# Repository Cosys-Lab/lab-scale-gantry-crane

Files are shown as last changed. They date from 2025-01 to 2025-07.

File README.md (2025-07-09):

# Lab-scale Gantry Crane Digital Twin Exemplar

This repository describes a lab-scale gantry crane digital twin exemplar. This exemplar was used in a couple of our [publications](#publications). This readme only contains basic information, for the complete documentation, head to [github pages](https://Cosys-Lab.github.io/lab-scale-gantry-crane/).

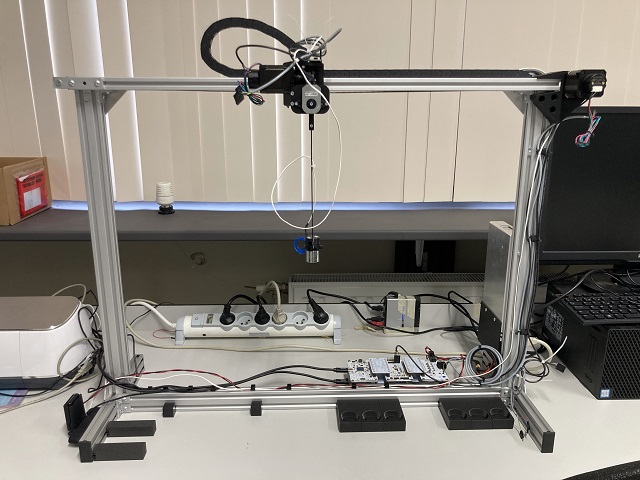
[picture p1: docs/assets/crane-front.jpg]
The gantry crane


The repository is structured as follows:

- [BOM](BOM/): the Bill-of-Materials of the crane.
- [C4-diagrams](C4-diagrams/): C4 diagrams of the crane's software used in the EDTConf submitted exemplar paper.
- [CAD](CAD/): CAD models of the crane in Fusion360, as well as 3MF exports for 3D printing.
- [arcadia](arcadia/): Capella models of the crane used in the SpaceRaise doctoral school.
- [arduino](arduino/): KiCad project of an optional Arduino shield that simplifies connecting the sensors of the crane, and accompanying code.
- [docker](docker/): A Docker compose file and associated files allowing for easy setup of the necessary background services.
- [docs](docs/): docs for creating the GitHub pages with MkDocs
- [examples](examples/): Examples of the Python module that controls the crane.
- [gantrylib](gantrylib/): The Python module controlling and monitoring the crane.
- [tests](tests/): Tests of the gantrylib module.

## Hardware Quickstart

Refer to the [build guide](https://cosys-lab.github.io/lab-scale-gantry-crane/build/) on GitHub Pages.

## Software Setup

### Python

Install Python. On Windows, preferably use Python 3.13 or higher, since earlier versions have a low resolution (only 15.6 ms) of the `time()` and `datetime.now()` functions, which are used often in the code.

Install the `gantrylib` module locally as editable installation. From the root of the repository folder, run:

    python -m pip install -e .

### Background services

The software relies on a TimescaleDB database, a Grafana dashboard and, optinally an MQTT broker. The setup files of all of these are contained in the [docker](docker/) folder. Assuming docker and docker compose are installed, from the docker folder, it suffices to run:

    docker compose up

The containers can then be started and stopped with:

    docker compose stop
    docker compose start

To remove the containers and the network connecting them, run:

    docker compose down

The config is exceptionally insecure, since all of the default usernames/passwords are used. If this is a problem, do change them.

#### TimeScaleDB
- address: localhost
- port: 5432
- user: postgres
- password: postgres
- database: gantrycrane

#### Grafana Dashboard
- address: localhost
- port: 3000
- user: admin
- password: admin (On first login via http://localhost:3000, you will be prompted to change the password. Nothing blocks you from reusing the old password though.)

#### MQTT
- address: localhost
- port: 1883
- user: not necessary, anonymous connections are allowed

The MQTT broker is really only needed if you want to run the TrajectoryGenerator service in its MQTT mode. Ofter services (Simulator, Validator) have in this release not yet been implemented in MQTT mode.

## Software quickstart

Assuming you went through the [software setup](#software-setup) and built the crane according to the [hardware quickstart](#hardware-quickstart), the fastest way to get the crane to do something is using the [run_with_hmi.py](examples/run_with_hmi.py) example. A short video demonstrating the example can be found on [youtube](https://youtu.be/BBAWoA0mC9U).

You will have to configure [crane-properties.yaml](examples/crane-properties.yaml) for your specific installation, more specifically, specify the serial ports of the two motor controller boards. Unfortunately, the Trinamic devkits don't offer a unique ID that allows you to identify them, therefore we recommend plugging in the boards one by one, and noting down the serial ports that appear as you plug them in (in `device manager/Ports (COM & LPT)` in Windows, or under `/dev/tty*` in Linux.)

Once you have noted down those ports, update the following two fields in the config:

    cart_motor_port: COM13
    ...
    hoist_motor_port: COM8

You can now run the example.

Upon first starting, it will home the cart and hoist motor. Homing the cart motor happens automatically, homing the hoist motor must be done with some manual user input. The script prompts you to confirm this on the command line. Afterwards you will see the simple HMI interface that allows you to move the crane.

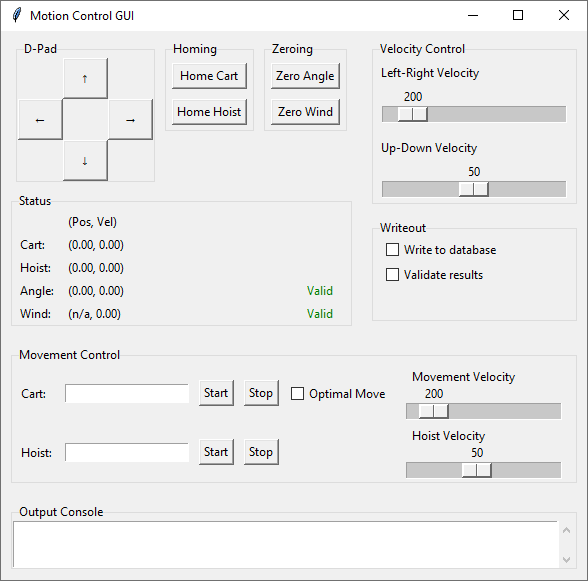
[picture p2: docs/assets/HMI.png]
HMI Screenshot


## Publications

Below are publications in which this exemplar was used:

1. J. Mertens and J. Denil, *Localizing Faults in Digital Twin Models by Using Time Series Classification Techniques*, 2024 Winter Simulation Conference (WSC), IEEE, Dec. 2024, pp. 2868–2879. [https://doi.org/10.1109/wsc63780.2024.10838825](https://doi.org/10.1109/wsc63780.2024.10838825)

2. J. Mertens, S. Klikovits, F. Bordeleau, J. Denil, and Ø. Haugen, *Continuous Evolution of Digital Twins using the DarTwin Notation*, Software and Systems Modeling, p. 22, Nov. 2024. [https://doi.org/10.1007/s10270-024-01216-7](https://doi.org/10.1007/s10270-024-01216-7)

3. J. Mertens and J. Denil, *Reusing model validation methods for the continuous validation of digital twins of cyber-physical systems*, Software and Systems Modeling, p. 23, Oct. 2024. [https://doi.org/10.1007/s10270-024-01225-6](https://doi.org/10.1007/s10270-024-01225-6)

4. J. Mertens and J. Denil, *Digital-twin Co-evolution using Continuous Validation*, In Proceedings of the ACM/IEEE 14th International Conference on Cyber-Physical Systems (with CPS-IoT Week 2023), ICCPS ’23, San Antonio, TX, USA: ACM, 2023, pp. 266–267. [https://doi.org/10.1145/3576841.3589628](https://doi.org/10.1145/3576841.3589628)

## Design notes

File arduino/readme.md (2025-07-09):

# Arduino

We use an Arduino Uno for monitoring and controlling the angle measuring encoder, the anemometer, the electromagnet (and the fischertechnik conveyor belt).

The folders contain:

- [arduino-shield-hardware](arduino-shield-hardware/)  
  The KiCad files of the optional Arduino shield.
- [arduino-shield-software](arduino-shield-software/)  
  The software to flash on the Arduino.
- [mqtt-wrapper](mqtt-wrapper/)  
  An MQTT wrapper around the Serial interface of the Arduino. Not needed when you only want to monitor the sensors.

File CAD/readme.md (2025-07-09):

# CAD

Contains the autodesk Fusion360 models of the crane. The [3MFs](3MFs/) folder contains exports of the 3D-printable files.

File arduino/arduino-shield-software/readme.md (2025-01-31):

Arduino code for an Arduino with the Conveyor shield V1.0 connected to 
the Fischertechnik conveyorbelt.

The command structure is described below

# G1 - Move indefinitely
## Description

The `G1` command moves the conveyor forwards or backwards indefinitely.

## Usage

`G1 [dir]`

### Parameters

[dir]: `F` for forwards, `B` for backwards.

## Example

`G1 F` # move forward indefinitely

# G2 - Move amount of pulses

## Description

The `G2` command moves the conveyor forwards or backwards a certain amount of pulses/steps.
one pulse is 1/8th of a rotatino of the conveyor's axle.

## Usage

`G1 [dir][pulses]`

### Parameters

[dir]: `F` for forwards, `B` for backwards.
[pulses]: number of pulses to move

## Example

`G1 F4` # move forward 4 pulses

# G3 - Move untill sensor

## Description

The `G3` command moves the conveyor forwards or backwards until the object
on the conveyor meets the start/end sensor.

## Usage

`G3 [dir]`

### Parameters

[dir]: `F` for forwards, `B` for backwards.

## Example

`G3 F` # move forward until the end sensor is triggered.

# G4 - Query Sensor State

## Description

The `G4` command queries the sensor (start, stop and pulse counter) state.

## Usage

`G4`

### Returns

`START_SENSOR: [1/0], END_SENSOR [1/0], PULSE_COUNT: [integer]`

## Example

`G4` # request sensor state
`START_SENSOR: 1, END_SENSOR 0, PULSE_COUNT: 40` # printer returns

# G5 - Stop movement

## Description

The `G5` command stops the conveyor.

## Usage

`G5`

# G6 - Electromagnet Control

## Description

The `G6` command controls the electromagnet

## Usage

`G6 [on/off]`

### Parameters

[on/off]: 0 to turn off, any other value to turn on.

## Example

`G6 1` # turn magnet on
`G6 0` # turn magnet off

# Other notes:

When a command is received that does not output data to the printer, 
it will return `OK [repeat command]` on the terminal

When an unknown command is received, it will return `NOK [repeat command]`

# Continuous angle output

The arduino also continuously measures the angle and the angular velocity
of the encoder and outputs it at a rate of 100 Hz.

This output has the shape `A: SX.XX,V: SY.YY`, where S is the optional
minus (-) sign, and the angle and angular velocity are printed with 2
decmial places. 

e.g. `A: -360.00,V: 10.15`

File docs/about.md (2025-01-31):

# about.md

Pages maintained by Joost Mertens
In case of question, feel free to get in touch by email or use the github issues: joost.mertens@uantwerpen.be

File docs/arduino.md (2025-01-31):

# arduino.md

## Prerequisites

Install following dependencies in the arduino IDE:

[Encoder](https://github.com/PaulStoffregen/Encoder)
[PinChangeInterrupt](https://github.com/NicoHood/PinChangeInterrupt/#pinchangeinterrupt-table)

## Explanation

In a nutshell: there are two arduino scripts

* one to measure angles with the encoder
* one to control the electromagnet (with additional functions)
    * this script requires you to build the arduino shield, for which KiCad files are provided.

In the future all of this code should be placed on one Arduino,
and the shield updated to a V2, which is future work.

## MQTT Wrapper

The shield was actually used to control a Fischertechnik conveyor belt with the arduino,
(to be detailled more) The command interface over serial can be found in the readme.md file in the folder.
We also provide an MQTT wrapper around it such that you can interface with Python or any other general purpose programming language.
TODO: document.

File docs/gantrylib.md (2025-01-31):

# gantrylib.md

## crane

### Crane

::: gantrylib.crane.Crane

## motors

### Motor

::: gantrylib.motors.Motor

### Stepper

::: gantrylib.motors.Stepper

### GantryStepper

::: gantrylib.motors.GantryStepper

### HoistStepper

::: gantrylib.motors.HoistStepper

## trajectory_generator

### TrajectoryGenerator

::: gantrylib.trajectory_generator.TrajectoryGenerator

## gantry_controller

## GantryController

::: gantrylib.gantry_controller.GantryController

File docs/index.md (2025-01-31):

# Lab Scale Gantry Crane Docs

crane-front

This is the documentation of the lab scale gantry crane. It is a little gantry crane that has been used in various papers as a demonstrator. The documentation covers the build of the crane, the accompanying `gantrylib` module and exmaples using this module.

## Documentation layout

* Home: this page
* Build: building instructions for the physical part of the crane.
* Arduino: documentation of the arduino scripts
* Examples: documentation of the examples
* gantrylib: api reference for the `gantrylib`

## Software prerequisites

### Installing gantrylib

The examples rely on the `gantrylib` module. Since there's no official release (yet) we recommend installing it in editable mode, this also allows for on the fly code changes. In the root of this repository run:

    python -m pip install -e .

We recommend doing so in a virtual environment.

### Arduino sketches

To open and flash the Arduino sketches you can install the [Arduino IDE](https://www.arduino.cc/)

### Opening CAD files

All CAD files are made with [Fusion360](https://www.autodesk.com/products/fusion-360/free-trial)
It's free for personal use. Your educational institution likely also has a license.

All files have already been exported to 3MF files, so you only need Fusion360 when you want to make edits.

### Viewing the docs offline

The docs are built with `MkDocs`. If you want to host those locally rather than view them on GitHub pages you should additionally install it.

    python -m pip install mkdocs mkdocstrings[python]

You can view the docs by running 

    mkdocs serve

Then opening http://127.0.0.1:8000/

## Hardware prerequisites

### 3D Printer

Some parts of the crane need to be 3D printed. To do so you need a 3D printer and accompanying slicer.

For reference: our parts where printed on Prusa i3 MK4's and sliced with [PrusaSlicer](https://www.prusa3d.com/page/prusaslicer_424/)

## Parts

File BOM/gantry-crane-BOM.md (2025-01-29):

# crane-BOM.md

## Bill of Materials (BOM)

This Bill of Materials (BOM) lists all the components required for this hardware project, including part numbers, descriptions, and suppliers.
This BOM in markdown format is generated from the original in Excel format. [BOM/crane_BOM.xlsx](../BOM/crane_BOM.xlsx)

### Sheet Hardware

| description                                            | supplier | supplier part number | quantity | price (€)         | total (€) | link                                                                                                                                                  |
|--------------------------------------------------------|----------|----------------------|----------|-------------------|-----------|-------------------------------------------------------------------------------------------------------------------------------------------------------|
| V-slot carriage                                        | ALUX     | V-slot gantry        | 1        | 5.95              | 5.95      | https://www.aluxprofiel.nl/v-slot-plaat/a4022                                                                                                         |
| 2040 cover plate                                       | ALUX     | 2040-cover           | 6        | 0.29              | 1.74      | https://www.aluxprofiel.nl/afdekkap-2040/a3586                                                                                                        |
| Aluminium profile 2040 V-slot 300mm                    | ALUX     | 2040                 | 2        | 1.99              | 3.98      | https://www.aluxprofiel.nl/aluminium-constructieprofiel-2040-v-slot/a3664                                                                             |
| Aluminium profile 2040 V-slot 560mm                    | ALUX     | 2040                 | 2        | 3.71              | 7.42      | https://www.aluxprofiel.nl/aluminium-constructieprofiel-2040-v-slot/a3664                                                                             |
| Aluminium profile 2040 V-slot 800mm                    | ALUX     | 2040                 | 1        | 5.3               | 5.3       | https://www.aluxprofiel.nl/aluminium-constructieprofiel-2040-v-slot/a3664                                                                             |
| Aluminium profile 2040 V-slot 760mm                    | ALUX     | 2040                 | 1        | 5.97              | 5.97      | https://www.aluxprofiel.nl/aluminium-constructieprofiel-2040-v-slot/a3664                                                                             |
| Connection plate Flat 20x80 - 4 holes                  | ALUX     | plate2080            | 1        | 0.69              | 0.69      | https://www.aluxprofiel.nl/verbindingsplaat-20x80/a3804                                                                                               |
| Connection plate T-shaped 60x60 - 5 holes              | ALUX     | T-plate6060          | 2        | 0.99              | 1.98      | https://www.aluxprofiel.nl/verbindingsplaat-t-60x60-5-gaten/a3810                                                                                     |
| Connection plate L-shaped 60x60 - 5 holes              | ALUX     | L-Plate6060          | 2        | 0.99              | 1.98      | https://www.aluxprofiel.nl/verbindingsplaat-l-60x60-5-gaten/a3809                                                                                     |
| Button head hex bolt M5x8                              | ALUX     | ISO 7380-M5x8        | 80       | 0.07              | 5.6       | https://www.aluxprofiel.nl/laagbolkopschroef-m5x8/a3794                                                                                               |
| T-slot nut M5                                          | ALUX     | 6-4-M5               | 80       | 0.2               | 16        | https://www.aluxprofiel.nl/inklikmoer-t-sleuf-6-m5/a3665                                                                                              |
| Rubber feet                                            | ALUX     | 9004                 | 6        | 0.79              | 4.74      | https://www.aluxprofiel.nl/rubber-voet/a3746                                                                                                          |
| Aluminium corner bracket 2020                          | ALUX     | 2020L-Alu            | 12       | 0.99              | 11.88     | https://www.aluxprofiel.nl/aluminium-verbindingshoek-2020/a3729                                                                                       |
| 2GT W6 Belt 2000mm                                     | 3DJake   | 2GT W6 2000 mm       | 1        | 5.83              | 5.83      | https://www.3djake.com/creality-3d-printers-spare-parts/belt-kit                                                                                      |
| 20 teeth 2GT Belt Pulley for 5mm shaft                 | 3DJake   | 2GT-20 5mm           | 1        | 2.49              | 2.49      | https://www.3djake.com/artillery/belt-pulley                                                                                                          |
| 625 2RS Bearing                                        | Conrad   | 198831 - 62          | 2        | 3.96              | 7.92      | https://www.conrad.be/nl/p/ubc-bearing-625-2rs-groefkogellager-radiaal-boordiameter-5-mm-buitendiameter-16-mm-toerental-max-24000-omw-min-198831.html |
| igus E-Kette® E2 micro Serie 06 06.10.018.0 Drag chain | Conrad   | 740611 - 62          | 1        | 28.09             | 28.09     | https://www.conrad.be/nl/p/igus-e-kette-e2-micro-serie-06-06-10-018-0-kabelrups-voor-kleine-buigradius-740611.html                                    |
| M2.5x8 countersunk bolt                                |          |                      | 1        |                   |           |                                                                                                                                                       |
| M2.5x12 bolt (can be countersunk or not)               |          |                      | 2        |                   |           |                                                                                                                                                       |
| M2.5x20 countersunk bolt                               |          |                      | 1        |                   |           |                                                                                                                                                       |
| M2.5 nut                                               |          |                      | 4        |                   |           |                                                                                                                                                       |
| M3x10 bolt (not countersunk)                           |          |                      | 10       |                   |           |                                                                                                                                                       |
| M3x20 countersunk bolt                                 |          |                      | 3        |                   |           |                                                                                                                                                       |
| M3 nut                                                 |          |                      | 2        |                   |           |                                                                                                                                                       |
| M4x12 countersunk bolt                                 |          |                      | 2        |                   |           |                                                                                                                                                       |
| M4x20 countersunk bolt                                 |          |                      | 2        |                   |           |                                                                                                                                                       |
| M4 nut                                                 |          |                      | 4        |                   |           |                                                                                                                                                       |
| M5x10 countersunk bolt                                 |          |                      | 2        |                   |           |                                                                                                                                                       |
| M5x16 countersunk bolt                                 |          |                      | 3        |                   |           |                                                                                                                                                       |
| M5x20 countersunk bolt                                 |          |                      | 2        |                   |           |                                                                                                                                                       |
| M5 nut                                                 |          |                      | 7        |                   |           |                                                                                                                                                       |
| Nuts and bolts: check fusion360 for dimensions         |          |                      |          |                   |           |                                                                                                                                                       |
|                                                        |          |                      |          | total (excl. VAT) | 117.56    |                                                                                                                                                       |

### Sheet - Electronics

| description                                                                       | supplier | supplier part number     | quantity | price (€)         | total (€) | link                                                                                                                           |
|-----------------------------------------------------------------------------------|----------|--------------------------|----------|-------------------|-----------|--------------------------------------------------------------------------------------------------------------------------------|
| Trinamic TMC4671-2A24V-EV-KIT (motor controller development kit)                  | Mouser   | 700-MC46712A24VEVKIT     | 2        | 297.53            | 595.06    | https://eu.mouser.com/ProductDetail/ADI-Trinamic/TMC4671-2A24V-EV-KIT?qs=TuK3vfAjtkVo6zoElLhaVQ%3D%3D                          |
| Trinamic QSH4218-51-10-049-10k stepper motor                                      | Mouser   | 700-QSH4218511004910     | 2        | 149.03            | 298.06    | https://eu.mouser.com/ProductDetail/ADI-Trinamic/QSH4218-51-10-049-10k?qs=QNEnbhJQKvbElhB2hkRfrg%3D%3D                         |
| Arduino Uno                                                                       | Mouser   | 782-A000066              | 2        | 26.22             | 52.44     | https://eu.mouser.com/ProductDetail/Arduino/A000066?qs=BC3YYPaifMrIue9b%252BHtKQg%3D%3D                                        |
| Molex 502380-0900 connector (for motors)                                          | Mouser   | 538-502380-0900          | 2        | 0.298             | 0.596     | https://eu.mouser.com/ProductDetail/Molex/502380-0900?qs=FtUJHUU4yUnSF7MTpEglZg%3D%3D                                          |
| Molex 502381-0000 pin (for motors)                                                | Mouser   | 538-502381-0000-CT       | 100      | 0.044             | 4.4       | https://eu.mouser.com/ProductDetail/Molex/502381-0000-Cut-Strip?qs=SMSg0crzni%2Fg42ifI25maw%3D%3D                              |
| Molex 16-02-0086  SL Crimp terminla female (for motor, motor drivers and encoder) | Mouser   | 538-70021-1021           | 100      | 0.079             | 7.9       | https://eu.mouser.com/ProductDetail/Molex/16-02-0086-Cut-Strip?qs=Ky1INM14uHolwHYRokZMPQ%3D%3D                                 |
| Molex 70021-1021 SL Crimp terminal male (for motors)                              | Mouser   | 538-16-02-0086-CT        | 100      | 0.079             | 7.9       | https://eu.mouser.com/ProductDetail/Molex/70021-1021?qs=PEbA6nSK%252BIWnZ1R%252Bv0zaCA%3D%3D                                   |
| Molex 50579405 SL Crimp housing (for AMT102 encoder)                              | Mouser   | 538-50-57-9405           | 1        | 0.314             | 0.314     | https://eu.mouser.com/ProductDetail/Molex/50-57-9405?qs=u6Gr9%2FNt%252B%2F%252BwqrO8nkfpaQ%3D%3D                               |
| Molex 50579005 SL Crimp housing (for motors and motor drivers)                    | Mouser   | 538-50-57-9005           | 6        | 0.447             | 2.682     | https://eu.mouser.com/ProductDetail/Molex/50-57-9005?qs=hSmm4fxMIuNcn%252B35N0E0lA%3D%3D                                       |
| Molex 50579002 SL Crimp housing (for electromagnet)                               | Mouser   | 538-50-57-9002           | 1        | 0.276             | 0.276     | https://eu.mouser.com/ProductDetail/Molex/50-57-9002?qs=hSmm4fxMIuPN0%252B32zyqW%252Bw%3D%3D                                   |
| Same Sky AMT102-V encoder                                                         | Mouser   | 490-AMT102-V             | 1        | 21.69             | 21.69     | https://eu.mouser.com/ProductDetail/Same-Sky/AMT102-V?qs=WyjlAZoYn533PQfgnorrMg%3D%3D                                          |
| Qualtek 764-00/002 AC Power Entry Module                                          | Mouser   | 562-764-00/002           | 1        | 7.52              | 7.52      | https://eu.mouser.com/ProductDetail/Qualtek/764-00-002?qs=uN5Dye%252BOwiXfVfVI0dfkHA%3D%3D                                     |
| Qualtek 364002-D01-HB1 AC Power cable                                             | Mouser   | 562-364002-HB1           | 1        | 8.36              | 8.36      | https://eu.mouser.com/ProductDetail/Qualtek/364002-D01-HB1?qs=tENXCkUKGaHfbZG0hkGDSQ%3D%3D                                     |
| Adafruit 5V Electromagnet                                                         | Mouser   | 485-3873                 | 1        | 9.25              | 9.25      | https://eu.mouser.com/ProductDetail/Adafruit/3873?qs=qSfuJ%252Bfl%2Fd4HCVDk1VD%2FzQ%3D%3D                                      |
| SparkFun Accessories XT60 Connectors Male/Female Pair                             | Mouser   | 474-PRT-10474            | 1        | 1.4               | 1.4       | https://eu.mouser.com/ProductDetail/SparkFun/PRT-10474?qs=WyAARYrbSnYJaRDMiD9g2w%3D%3D                                         |
| 24V Power Supply for Creality Ender 3 s1                                          | 3DJake   | Power Supply, Ender 3 s1 | 1        | 40.32             | 40.32     | https://www.3djake.com/creality-3d-printers-spare-parts/power-supply-1?sai=14488                                               |
| Kabeltronik Sensorcable Sensocord® 5 x 0.09 mm² (quantity in meters)              | Conrad   | 323819 - 62              | 5        | 5.78              | 28.9      | https://www.conrad.be/nl/p/kabeltronik-24205d800-1-sensorkabel-sensocord-5-x-0-09-mm-zwart-per-meter-323819.html               |
| Kabeltronik PURtronic Highflex cable 4 x 0.14 mm² (quantity in meters)            | Conrad   | 486529 - 62              | 3        | 4.95              | 14.85     | https://www.conrad.be/nl/p/kabeltronik-purtronic-highflex-stuurstroomkabel-4-x-0-14-mm-grijs-213041400-1-per-meter-486529.html |
| Lenovo USB-C to 4 Port USB-A Hub USB-C                                            | Conrad   | 2886621 - 62             | 1        | 14.87             | 14.87     | https://www.conrad.be/nl/p/lenovo-usb-c-to-4-port-usb-a-hub-usb-c-usb-3-2-gen-1-multiport-hub-4-poorten-zwart-2886621.html     |
| Wiring from power supply to motor controllers. 2x16 AWG suffices                  |          |                          |          |                   |           |                                                                                                                                |
| Wiring to electromagnet, thinner cable with 2x24 AWG suffices                     |          |                          |          |                   |           |                                                                                                                                |
|                                                                                   |          |                          |          | total (excl. VAT) | 1116.788  |                                                                                                                                |

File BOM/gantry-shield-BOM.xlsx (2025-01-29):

article | description | qty | price | subtotal | link
637-1N4007 | 1N4007 | 1 | 0.093 | 0.093 | https://www.mouser.be/ProductDetail/Diotec-Semiconductor/1N4007?qs=OlC7AqGiEDmK9mU1uTiCkg%3D%3D
651-1757242 | MSTBA 2,5/ 2-G-5,08 - PCB header | 1 | 0.54 | 0.54 | https://eu.mouser.com/ProductDetail/Phoenix-Contact/1757242?qs=uD%2FdkN7XIa3Ejiz9qDxlzw%3D%3D
651-1757019 | MSTB 2,5/ 2-ST-5,08 - PCB connector | 1 | 2.02 | 2.02 | https://eu.mouser.com/ProductDetail/Phoenix-Contact/1757019?qs=cq3Rj917t3lqr5dPgsHAsg%3D%3D
710-61202621621 | 61202621621 | 1 | 1.03 | 1.03 | https://eu.mouser.com/ProductDetail/Wurth-Elektronik/61202621621?qs=ZtY9WdtwX57AwIRbd5IHkA%3D%3D
710-61202623021 | 61202623021 | 2 | 1.47 | 2.94 | https://eu.mouser.com/ProductDetail/Wurth-Elektronik/61202623021?qs=ZtY9WdtwX57g2sRCs8B%2Fgw%3D%3D
517-3365/26FT | 3365/26-CUT-LENGTH | 1 | 1.15 | 1.15 | https://eu.mouser.com/ProductDetail/3M-Electronic-Solutions-Division/3365-26-CUT-LENGTH?qs=QV10cN0MjFu22vZzOnogAw%3D%3D
522-BS170FTA | BS170F | 1 | 0.632 | 0.632 | https://eu.mouser.com/ProductDetail/Diodes-Incorporated/BS170FTA?qs=%2FU6xRUa2FMDXziIHYnqHVQ%3D%3D
595-TL084HIDR | TL084 SOIC14 | 1 | 0.28 | 0.28 | https://eu.mouser.com/ProductDetail/Texas-Instruments/TL084HIDR?qs=81r%252BiQLm7BTThBPvzBazbA%3D%3D
603-MFR-25FTF52-220R | 220 ohms | 1 | 0.093 | 0.093 | https://eu.mouser.com/ProductDetail/YAGEO/MFR-25FTF52-220R?qs=gt1LBUVyoHnXPrJ70Ki%252BVg%3D%3D
603-MFR-25FTF52-100K | 100k | 5 | 0.093 | 0.465 | https://eu.mouser.com/ProductDetail/YAGEO/MFR-25FTF52-100K?qs=OXzh9Ga2KBF%252BJCQIIZKMHQ%3D%3D
603-MFR-25FTF52-22K | 22k | 4 | 0.093 | 0.372 | https://eu.mouser.com/ProductDetail/YAGEO/MFR-25FTF52-22K?qs=gt1LBUVyoHkUynDsTgGFYw%3D%3D
603-MFR-25FTF52-10K | 10k | 1 | 0.093 | 0.093 | https://eu.mouser.com/ProductDetail/YAGEO/MFR-25FTF52-10K?qs=NNLo%2FHOmKML%2FcyMBYbmnXA%3D%3D
474-PRT-10007 | PRT-10007 | 1 | 1.51 | 1.51 | https://eu.mouser.com/ProductDetail/SparkFun/PRT-10007?qs=WyAARYrbSnYGf8RckgedYg%3D%3D
530-SC-2ABE003F | USB B cable | 1 | 2.26 | 2.26 | https://eu.mouser.com/ProductDetail/Stewart-Connector-Bel/SC-2ABE003F?qs=r5DSvlrkXmIbaXte8fNdQA%3D%3D
 |  |  | total | 13.478

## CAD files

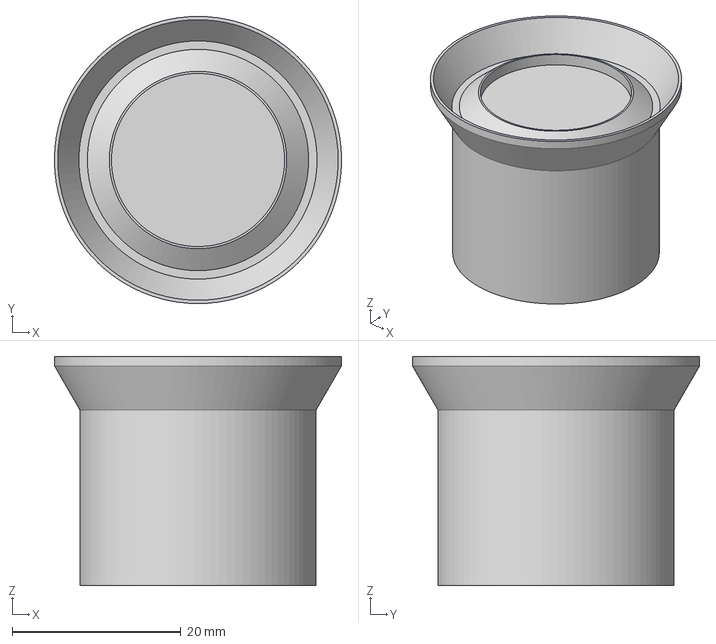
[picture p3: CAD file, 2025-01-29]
CAD/3MFs/stackable-container.3mf
34.0 x 34.0 x 27.1 mm

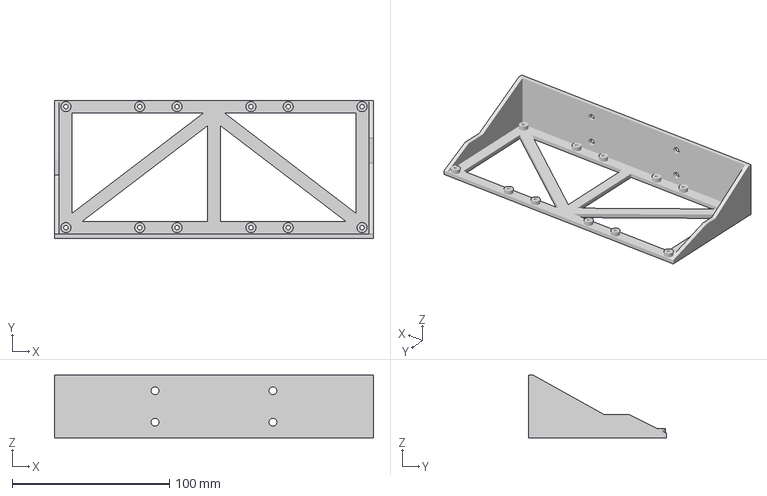
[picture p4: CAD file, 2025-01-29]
CAD/3MFs/motor-driver-mount.3mf
203.0 x 88.0 x 40.0 mm

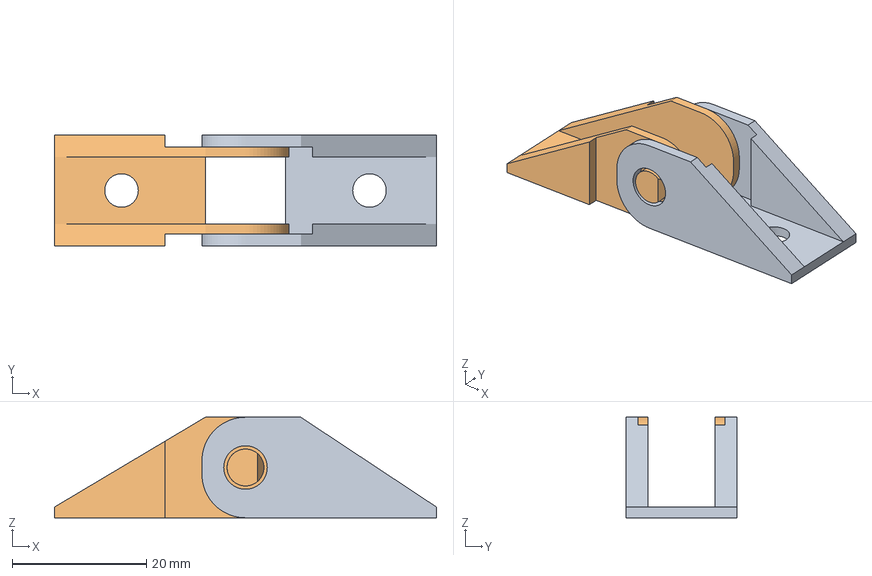
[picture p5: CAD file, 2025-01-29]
CAD/3MFs/chain-link-ends.3mf
57.0 x 16.5 x 15.0 mm

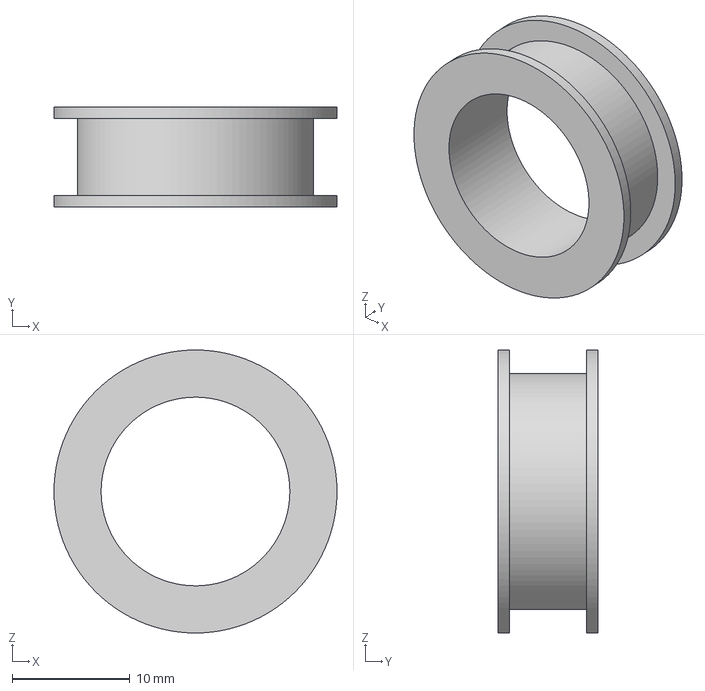
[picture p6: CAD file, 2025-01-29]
CAD/3MFs/idler-pulley.3mf
24.0 x 8.50 x 24.0 mm

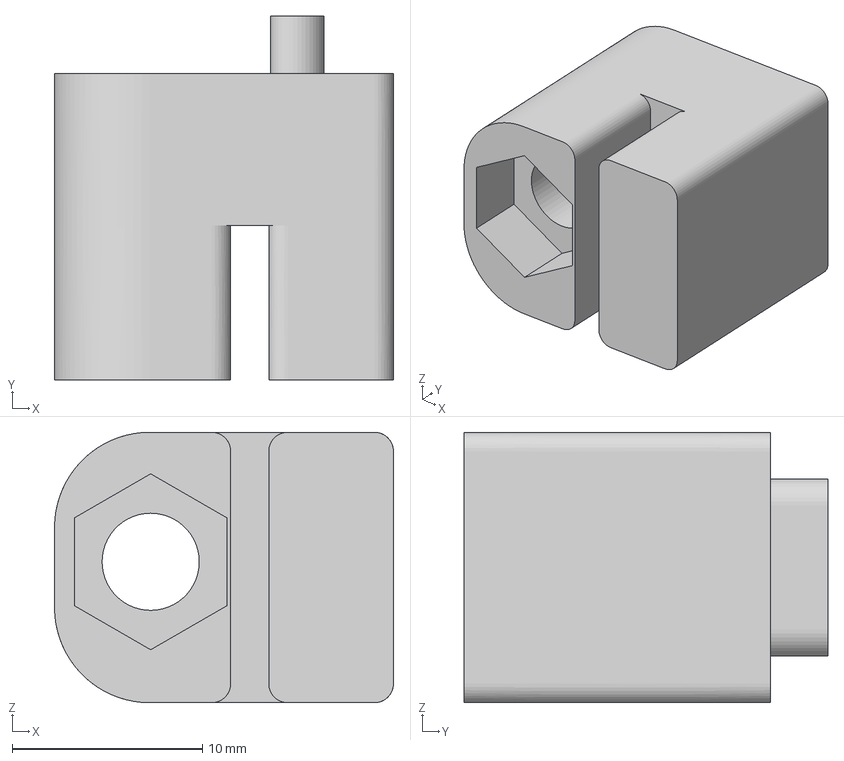
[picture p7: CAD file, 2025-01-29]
CAD/3MFs/belt-holder.3mf
17.8 x 19.1 x 14.2 mm

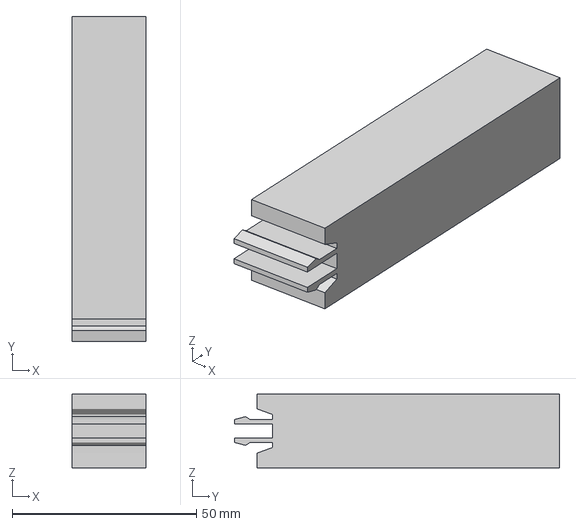
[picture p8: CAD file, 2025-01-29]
CAD/3MFs/conveyor-spacer-82mm.3mf
20.0 x 88.1 x 20.0 mm

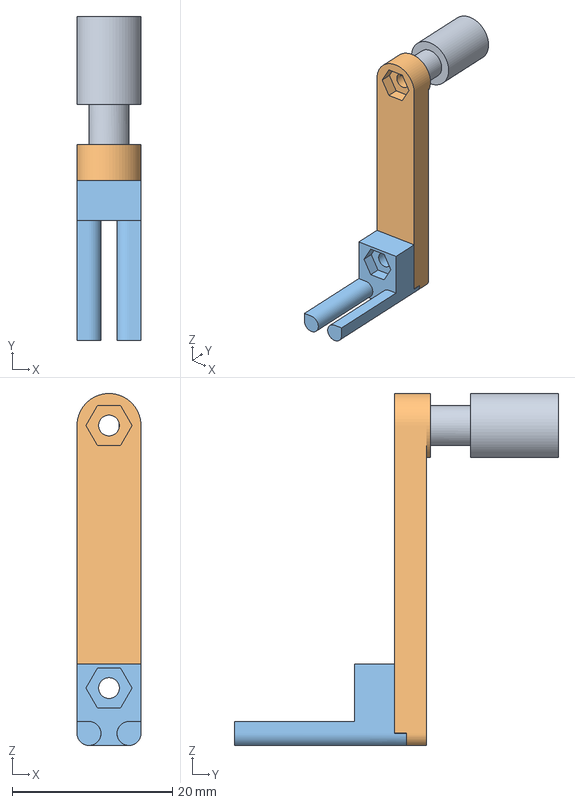
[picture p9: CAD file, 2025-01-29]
CAD/3MFs/rope-feeler.3mf
8.00 x 40.5 x 44.0 mm

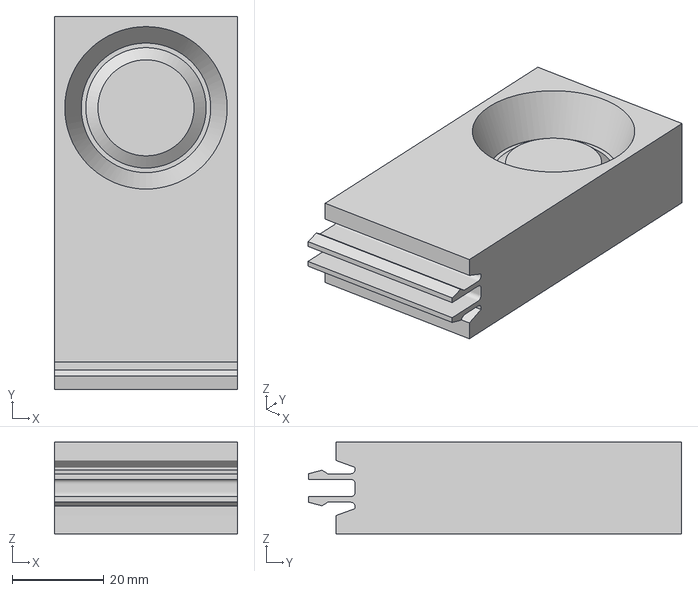
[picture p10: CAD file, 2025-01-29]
CAD/3MFs/container-baseplate.3mf
40.0 x 81.6 x 20.0 mm

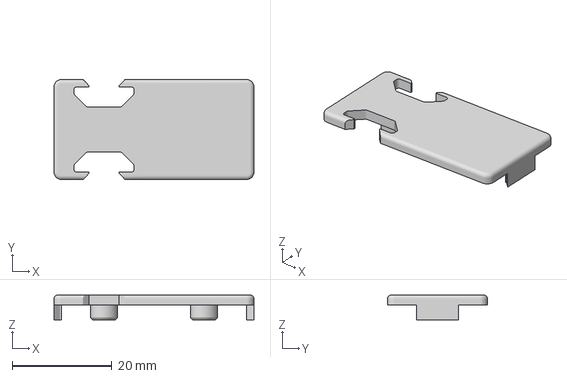
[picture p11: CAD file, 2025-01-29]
CAD/3MFs/vslot-cover-B.3mf
40.0 x 20.0 x 5.00 mm

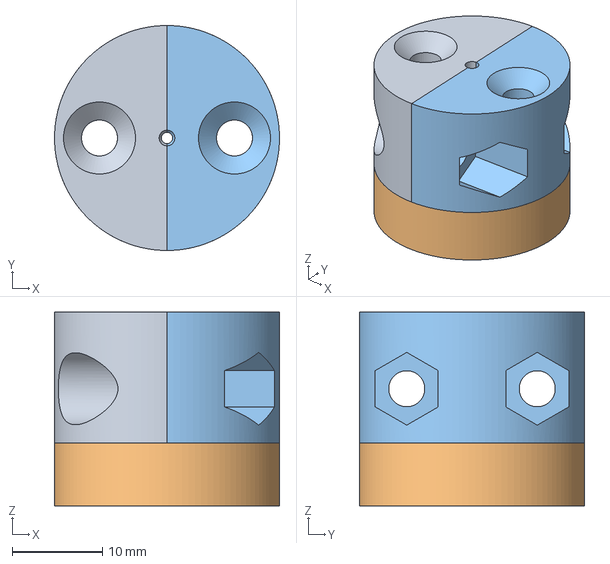
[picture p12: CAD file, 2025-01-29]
CAD/3MFs/electromagnet-gripper.3mf
25.0 x 25.0 x 21.5 mm

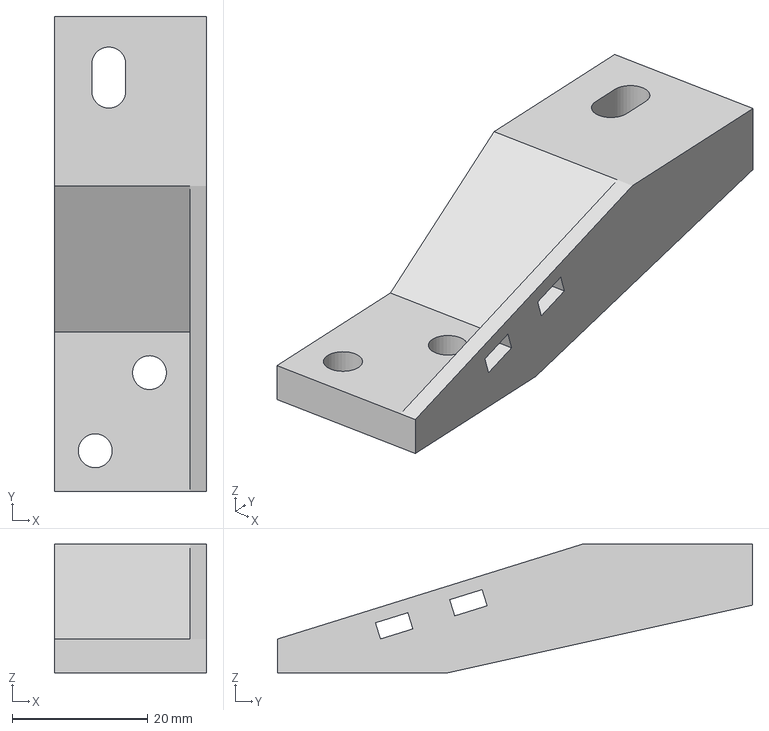
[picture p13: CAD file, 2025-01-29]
CAD/3MFs/cable carrier mount.3mf
22.4 x 70.0 x 19.0 mm

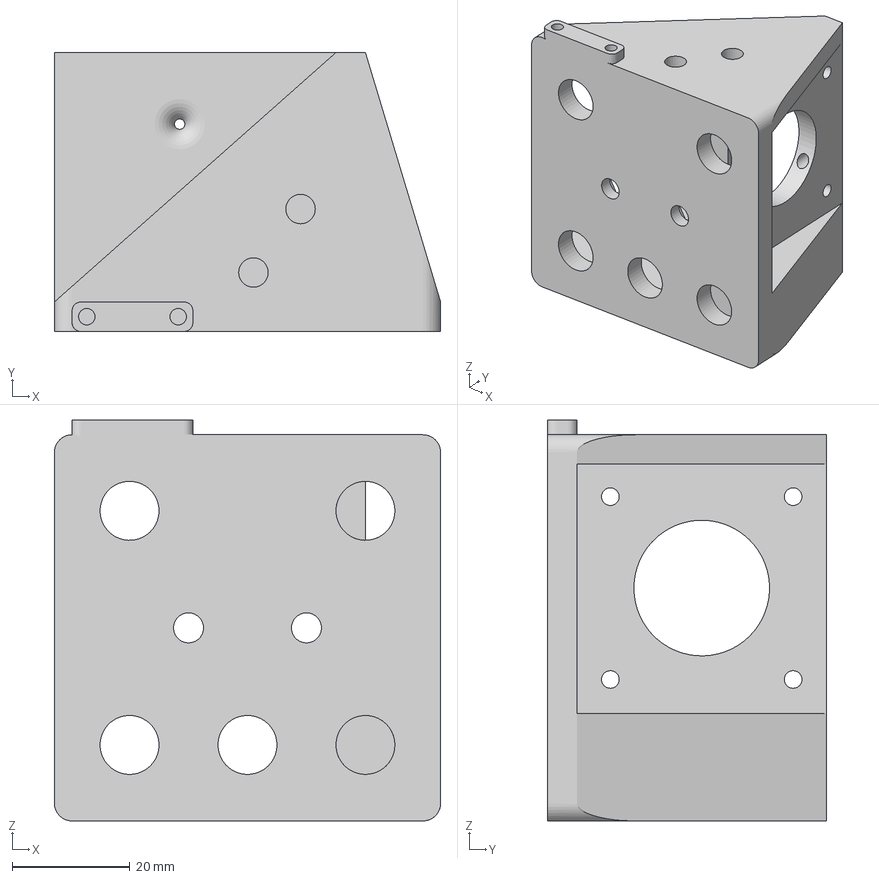
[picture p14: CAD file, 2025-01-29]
CAD/3MFs/hoist-motor-holder.3mf
65.5 x 47.3 x 68.0 mm

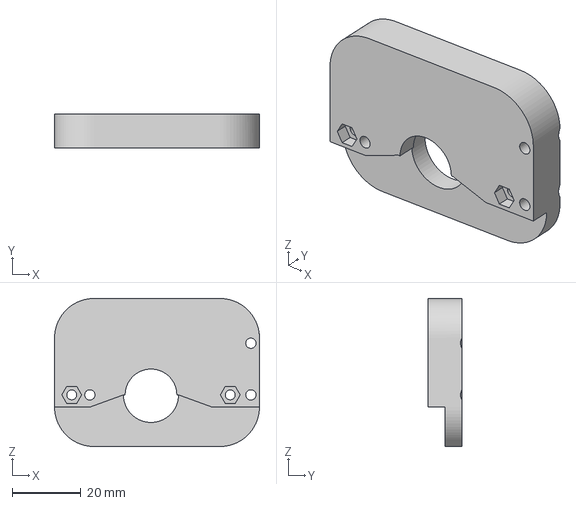
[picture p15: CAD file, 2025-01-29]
CAD/3MFs/sensor-mounting-plate.3mf
59.5 x 10.0 x 43.0 mm

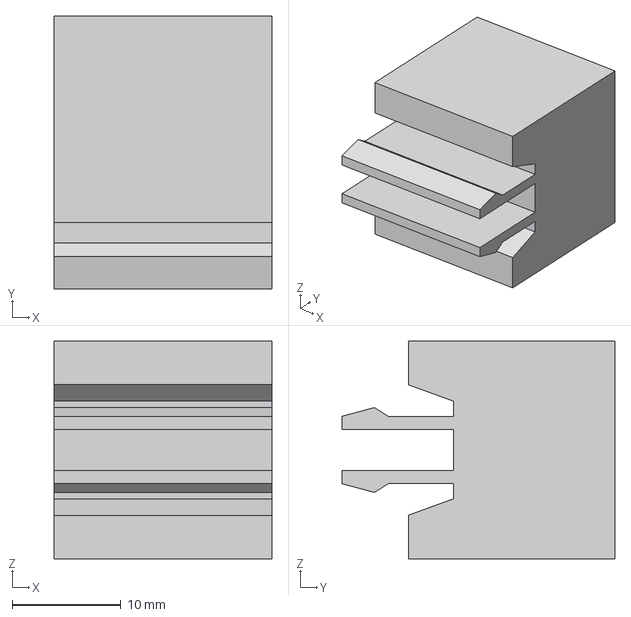
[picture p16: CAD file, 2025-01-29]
CAD/3MFs/conveyor-spacer-19mm.3mf
20.0 x 25.1 x 20.0 mm

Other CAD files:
CAD/3MFs/belt-holder(Mirror).3mf
CAD/3MFs/vslot-cover-A.3mf
CAD/3MFs/rope-drum.3mf
CAD/3MFs/motor-mount.3mf
CAD/V-Slot Gantry.f3d
CAD/chain-link-ends.f3d
CAD/container-baseplate.f3d
CAD/conveyor-spacer.f3d
CAD/electromagnet-gripper.f3d
CAD/gantry-crane-aluminium-extrusion.f3z
CAD/hoist.f3z
CAD/idler-pulley.f3d
CAD/motor-driver-mount.f3d
CAD/motor-mount.f3d
CAD/rope-drum.f3d
CAD/stackable-container.f3d
CAD/vslot-cover-A.f3d
CAD/vslot-cover-B.f3d

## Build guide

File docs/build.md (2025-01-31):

# build.md

## Building instructions.

TODO: complete this further.

For now: refer to the Fusion360 files.

## Screws

The following images try to convey which bolts and nuts are needed at which spots in the crane.
I will edit these in the future to have annotation on them.

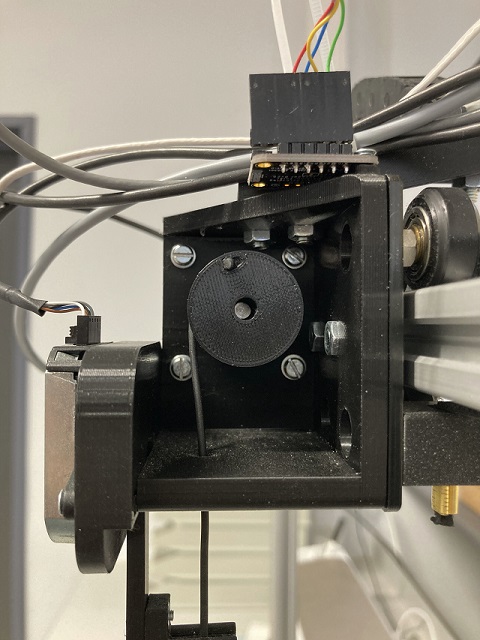
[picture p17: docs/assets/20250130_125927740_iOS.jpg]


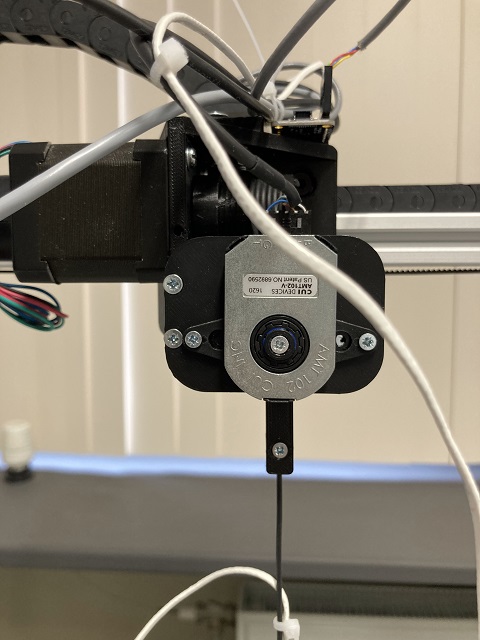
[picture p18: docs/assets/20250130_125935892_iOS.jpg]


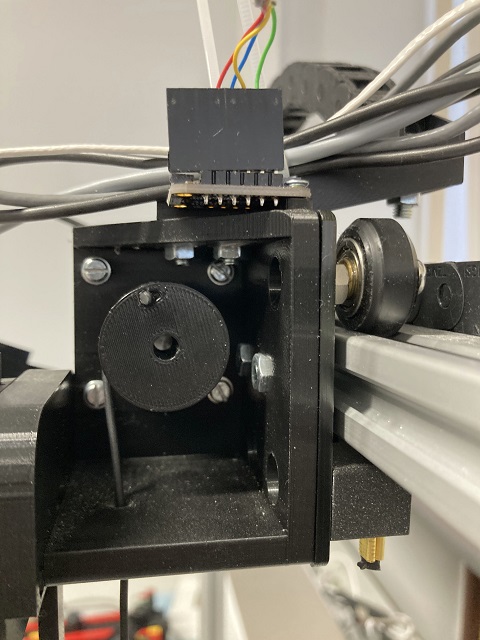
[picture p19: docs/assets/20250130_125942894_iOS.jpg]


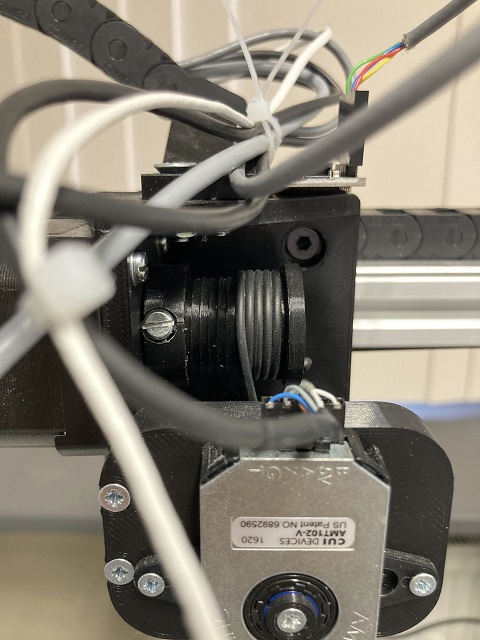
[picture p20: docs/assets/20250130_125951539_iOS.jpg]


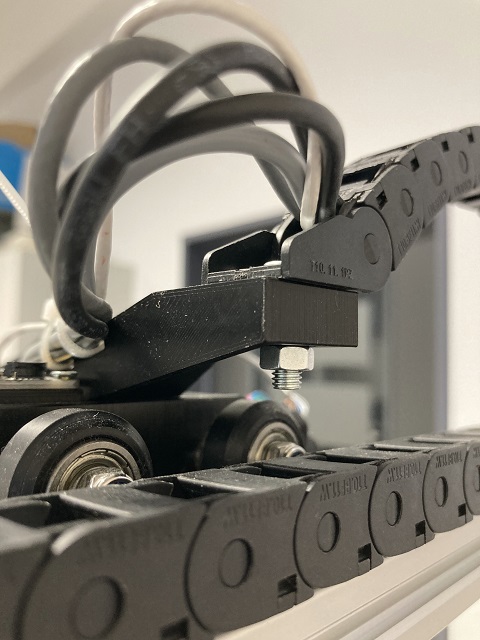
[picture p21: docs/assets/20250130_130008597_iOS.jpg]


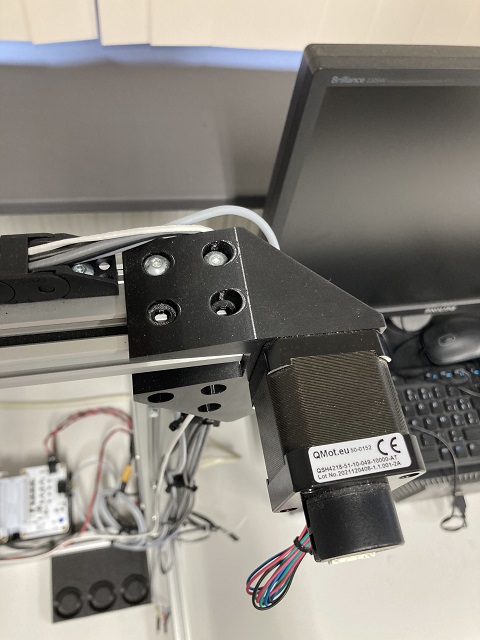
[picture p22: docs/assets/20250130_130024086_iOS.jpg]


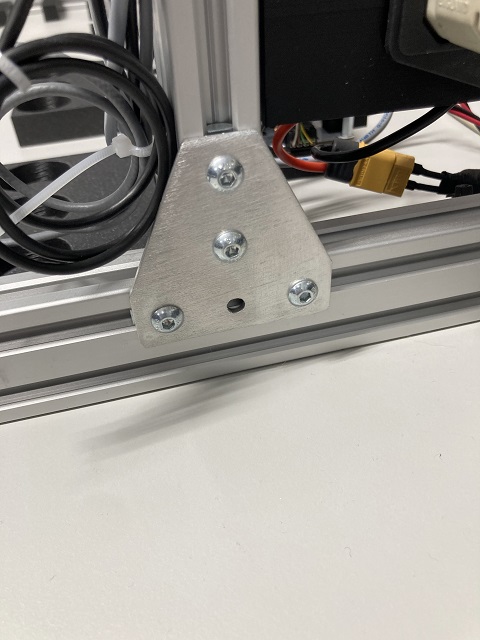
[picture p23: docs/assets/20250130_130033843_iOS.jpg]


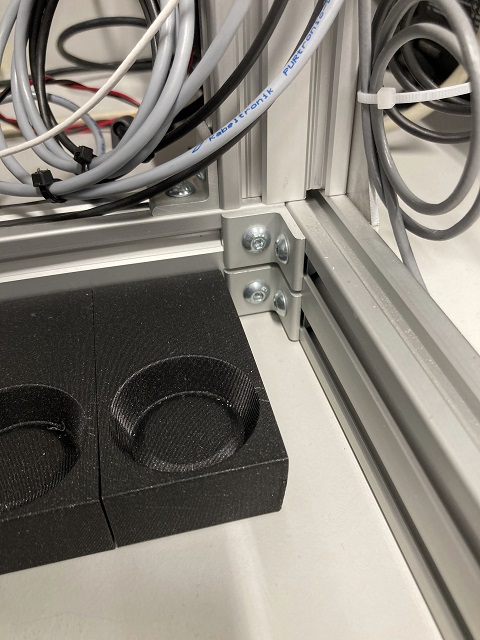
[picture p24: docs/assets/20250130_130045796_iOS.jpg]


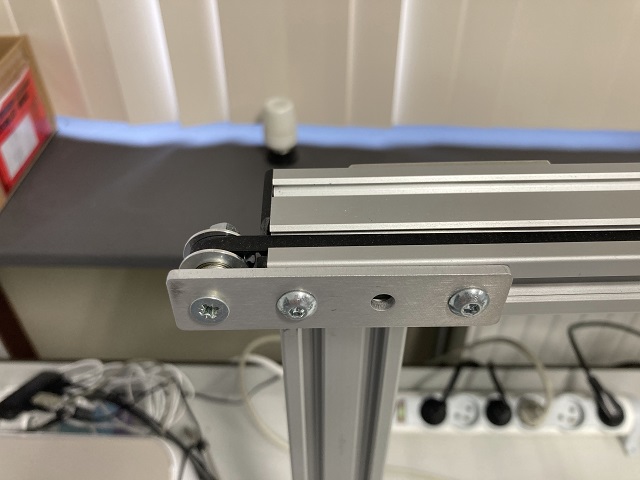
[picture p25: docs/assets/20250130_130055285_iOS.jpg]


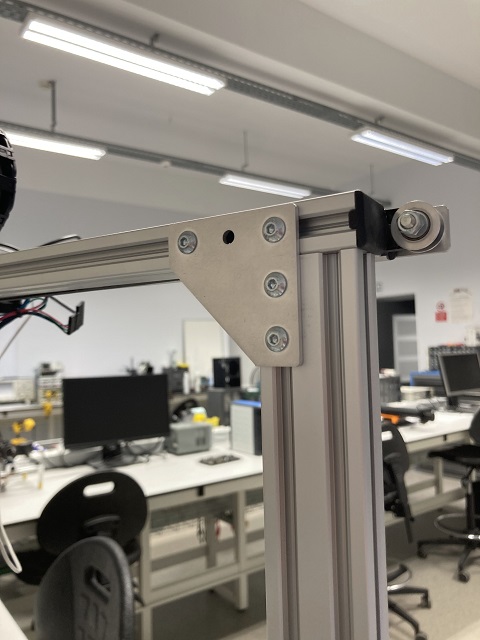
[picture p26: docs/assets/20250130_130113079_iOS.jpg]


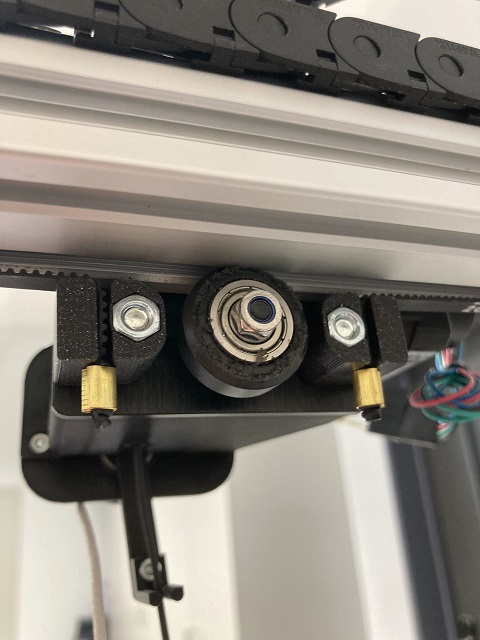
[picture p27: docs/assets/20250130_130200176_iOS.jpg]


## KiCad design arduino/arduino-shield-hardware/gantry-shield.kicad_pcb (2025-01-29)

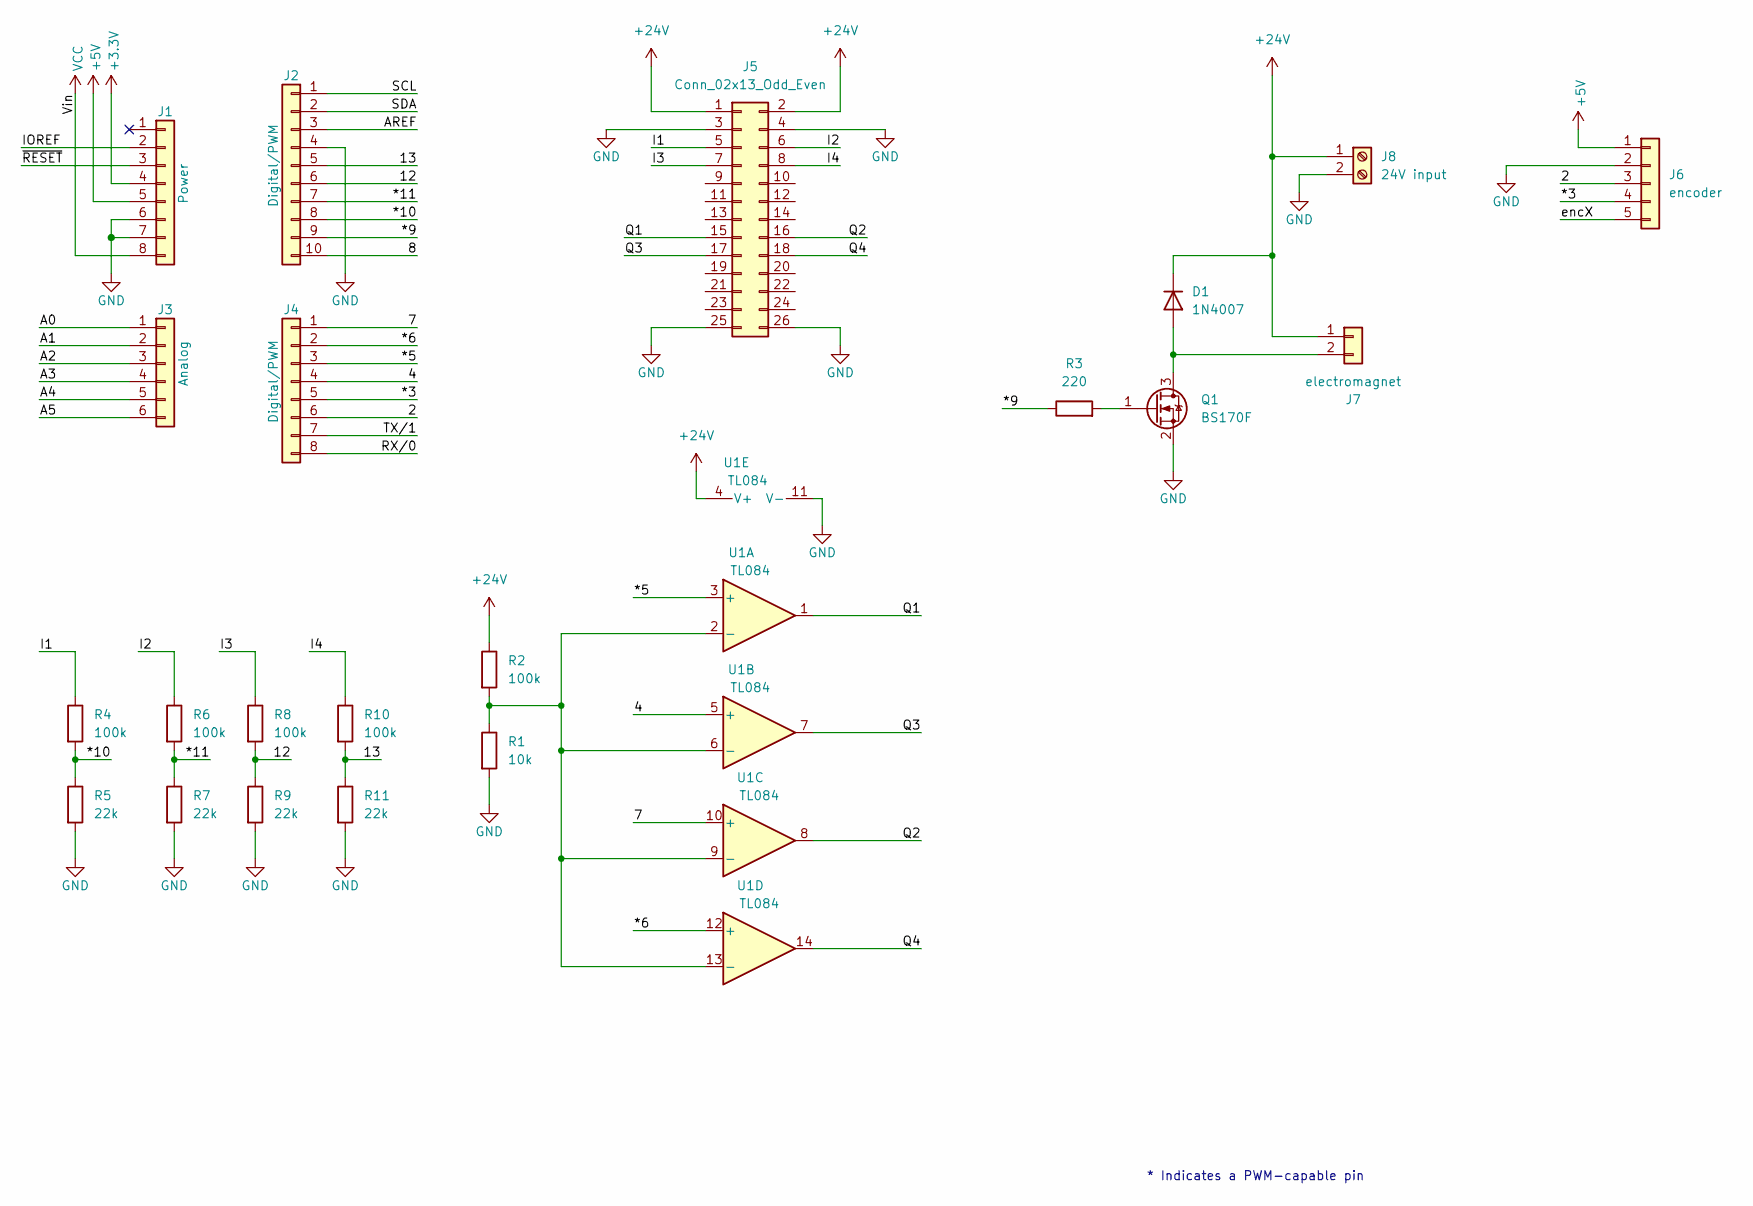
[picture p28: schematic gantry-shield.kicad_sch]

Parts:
D1: 1N4007; D_DO-41_SOD81_P10.16mm_Horizontal
J1: Power; PinSocket_1x08_P2.54mm_Vertical
J2: Digital/PWM; PinSocket_1x10_P2.54mm_Vertical
J3: Analog; PinSocket_1x06_P2.54mm_Vertical
J4: Digital/PWM; PinSocket_1x08_P2.54mm_Vertical
J5: Conn_02x13_Odd_Even; IDC-Header_2x13_P2.54mm_Vertical
J6: encoder; PinHeader_1x05_P2.54mm_Vertical
J7: electromagnet; PinHeader_1x02_P2.54mm_Vertical
J8: 24V input; PhoenixContact_MSTBA_2,5_2-G-5,08_1x02_P5.08mm_Horizontal
Q1: BS170F; SOT-23
R1: 10k; R_Axial_DIN0207_L6.3mm_D2.5mm_P10.16mm_Horizontal
R2, R4, R6, R8, R10: 100k; R_Axial_DIN0207_L6.3mm_D2.5mm_P10.16mm_Horizontal
R3: 220; R_Axial_DIN0207_L6.3mm_D2.5mm_P10.16mm_Horizontal
R5, R7, R9, R11: 22k; R_Axial_DIN0207_L6.3mm_D2.5mm_P10.16mm_Horizontal
U1: TL084; SOIC-14_3.9x8.7mm_P1.27mm

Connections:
+3V3: J1.4
+5V: J1.5, J6.1
+24V: D1.1 (K), J5.1, J5.2, J7.1, J8.1, R2.1, U1.4 (V+)
/2: J4.6, J6.3
/4: J4.4, U1.5 (+)
/7: J4.1, U1.10 (+)
/8: J2.10
/12: J2.6, R8.2, R9.1
/13: J2.5, R10.2, R11.1
/*3: J4.5, J6.4
/*5: J4.3, U1.3 (+)
/*6: J4.2, U1.12 (+)
/*9: J2.9, R3.1
/*10: J2.8, R4.2, R5.1
/*11: J2.7, R6.2, R7.1
/A0: J3.1
/A1: J3.2
/A2: J3.3
/A3: J3.4
/A4: J3.5
/A5: J3.6
/AREF: J2.3
/I1: J5.5, R4.1
/I2: J5.6, R6.1
/I3: J5.7, R8.1
/I4: J5.8, R10.1
/IOREF: J1.2
/Q1: J5.15, U1.1
/Q2: J5.16, U1.8
/Q3: J5.17, U1.7
/Q4: J5.18, U1.14
/RX/0: J4.8
/SCL: J2.1
/SDA: J2.2
/TX/1: J4.7
/encX: J6.5
/~RESET: J1.3
GND: J1.6, J1.7, J2.4, J5.3, J5.4, J5.25, J5.26, J6.2, J8.2, Q1.2 (S), R1.2, R5.2, R7.2, R9.2, R11.2, U1.11 (V-)
unnamed: D1.2 (A), J7.2, Q1.3 (D)
unnamed: Q1.1 (G), R3.2
unnamed: R1.1, R2.2, U1.2 (-), U1.6 (-), U1.9 (-), U1.13 (-)
VCC: J1.8

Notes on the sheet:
* Indicates a PWM-capable pin

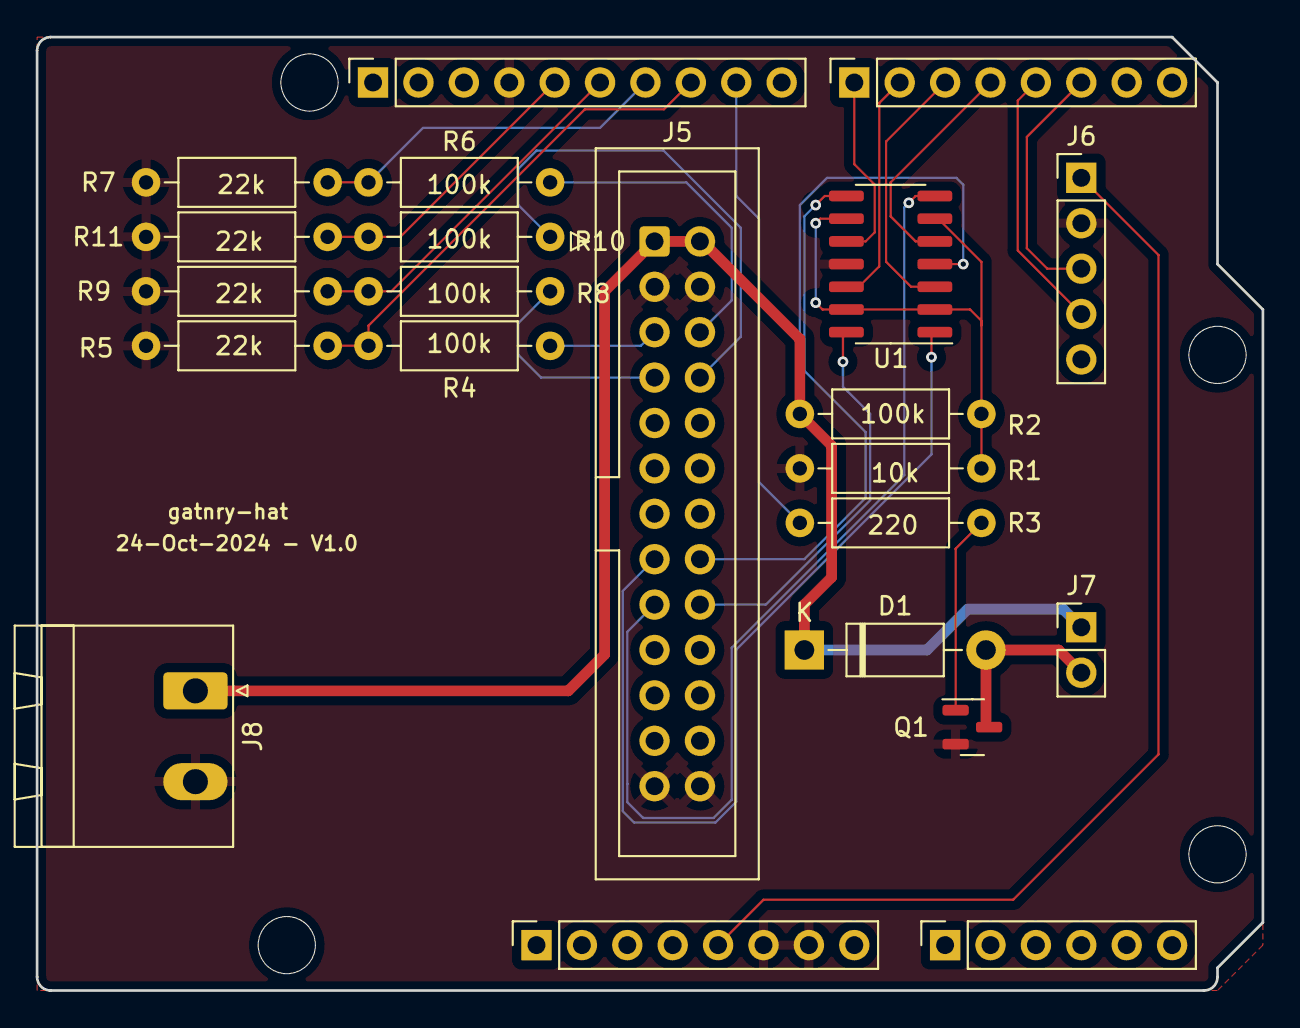
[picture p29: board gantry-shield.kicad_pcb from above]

Board: 2 copper layers, 68.6 x 53.3 mm, 26 parts (0 on the bottom side), 25 nets.

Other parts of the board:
MH1, MH2, MH3, MH4: MountingHole_3.2mm

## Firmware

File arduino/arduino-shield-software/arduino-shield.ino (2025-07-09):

#include "Encoder.h"
#include "PinChangeInterrupt.h"

#define START_SENSOR_PIN 10
#define END_SENSOR_PIN 11
#define PULSE_SENSOR_PIN 12
#define FORWARD_PIN 5
#define BACKWARD_PIN 7
#define ELECTROMAGNET_PIN 9
#define ANEMOMETER_PIN A0

#define DEBOUNCE_THRESHOLD 10 // Number of consecutive stable samples required

volatile bool runDebounce = false;
bool usingInterrupt = false;
volatile unsigned long pulseCount = 0;
volatile unsigned long targetPulseCount = 0;
volatile bool stopAtSensor = false;
volatile int sensorToStopAt = 0;
volatile bool moveCompleted = false;
bool conveyorRunning = false;
int conveyorDirection = 0;  // 1 for forward, -1 for backward, 0 for stopped
unsigned long prev_millis = 0;
unsigned long prev_millis_angle = 0;

String commandBuffer = ""; // Buffer to store the command

/* Set up the Encoder object */
Encoder angleMeter(2,3);

// Scaling variable to convert counts to degrees
float counts_to_deg = 360.0/8096.0;

long prev_angle = 0;
long prev_time = 0;
float angle = 0;
float angular_vel = 0;
float angular_vel_smooth = 0;
float wspeed = 0;

// anemometer things
int anemometer_zero = 0;

// Function prototypes
void setup();
void loop();
void processCommand(String command);
void startConveyor(int direction);
void stopConveyor();
void movePulses(int direction, unsigned long pulses);
void moveToSensor(int direction, int sensorPin);
void querySensors();
//void pulseISR();
void startSensorISR();
void stopSensorISR();
void debouncePulse();
void pulseCheck();
void setElectroMagnet(int onOff);
void updateAngle();
void printHuman();
void printMachine();

void setup() {
  Serial.begin(115200);
  pinMode(START_SENSOR_PIN, INPUT);
  pinMode(END_SENSOR_PIN, INPUT);
  pinMode(PULSE_SENSOR_PIN, INPUT);
  pinMode(FORWARD_PIN, OUTPUT);
  pinMode(BACKWARD_PIN, OUTPUT);
  pinMode(ELECTROMAGNET_PIN, OUTPUT); // important!
  setElectroMagnet(0);
  pinMode(ANEMOMETER_PIN, INPUT);
  anemometer_zero = analogRead(ANEMOMETER_PIN); // zero reading (make sure no wind is there at bootup!)

  attachPinChangeInterrupt(digitalPinToPinChangeInterrupt(START_SENSOR_PIN), startSensorISR, FALLING);
  attachPinChangeInterrupt(digitalPinToPinChangeInterrupt(END_SENSOR_PIN), stopSensorISR, FALLING);
  //attachPinChangeInterrupt(digitalPinToPinChangeInterrupt(PULSE_SENSOR_PIN), pulseISR, CHANGE); too bouncy to be used inside an ISR unfortunately

  prev_time = millis();
}

void loop() {
  while (Serial.available() > 0) {
    char receivedChar = Serial.read();
    Serial.print(receivedChar);
    commandBuffer += receivedChar;
    if (receivedChar == '\n') {
      commandBuffer.trim();
      processCommand(commandBuffer);
      commandBuffer = ""; // Clear the buffer after processing the command
    }
  }

  // debounce pulse every 1 ms, 50 consecutive bounces seems like a good value?
  // breaks if the arduino operates for more than 50 days.
  if(millis() > prev_millis){
    debouncePulse();
    prev_millis = millis();
  }
  // update as fast as possible
  updateAngle();
  // output at 100 Hz?
  if(millis() > prev_millis_angle+10){
    prev_millis_angle = millis();
    wspeed = (analogRead(ANEMOMETER_PIN) - anemometer_zero) * (32.4 - 0) / (410 - anemometer_zero) + 0;
    printHuman();
    printMachine();
  }
  
  pulseCheck();
}

void processCommand(String command) {
  if (command.startsWith("G1")) {
    // Example: G1 F (Forward indefinitely)
    //          G1 B (Backward indefinitely)
    char direction = command.charAt(3);
    if (direction == 'F') {
      if (conveyorRunning)
      {
        stopConveyor();
      }
      
      startConveyor(1);
      Serial.println("OK " + command);
    } else if (direction == 'B') {
        if (conveyorRunning)
      {
        stopConveyor();
      }
      startConveyor(-1);
      Serial.println("OK " + command);
    }
  } else if (command.startsWith("G2")) {
    // Example: G2 F 100 (Forward 100 pulses)
    char direction = command.charAt(3);
    int targetPulses = command.substring(5).toInt();
    if (direction == 'F') {
      movePulses(1, targetPulses);
      Serial.println("OK " + command);
    } else if (direction == 'B') {
      movePulses(-1, targetPulses);
      Serial.println("OK " + command);
    }
  } else if (command.startsWith("G3")) {
    // Example: G3 F (Forward until the payload reaches the end sensor)
    char direction = command.charAt(3);
    if (direction == 'F') {
      moveToSensor(1, END_SENSOR_PIN);
      Serial.println("OK " + command);
    } else if (direction == 'B') {
      moveToSensor(-1, START_SENSOR_PIN);
      Serial.println("OK " + command);
    }
  } else if (command.startsWith("G4")) {
    // Example: G4 (Query sensor states)
    querySensors();
  } else if (command.startsWith("G5")) {
    // Example: G5 (Stop the conveyor)
    stopConveyor();
    Serial.println("OK G5");
  } else if (command.startsWith("G6")) {
    // add code for the electromagnet -> do experimentation for current and dutycycle first.
    int target = command.substring(3).toInt();// 0 = off >0 = on
    setElectroMagnet(target);
  } else {
    Serial.println("NOK " + command);
  }
}

void startConveyor(int direction) {
  conveyorDirection = direction;
  conveyorRunning = true;
  if (direction == 1) {
    digitalWrite(FORWARD_PIN, HIGH);
  } else if (direction == -1) {
    digitalWrite(BACKWARD_PIN, HIGH);
  }
}

void stopConveyor() {
  digitalWrite(FORWARD_PIN, LOW);
  digitalWrite(BACKWARD_PIN, LOW);
  conveyorRunning = false;
  conveyorDirection = 0;
  targetPulseCount = 0;
  stopAtSensor = false;
}

void movePulses(int direction, unsigned long pulses) {
    if (conveyorRunning){
        stopConveyor();
    }
    pulseCount = 0;
    targetPulseCount = pulses;
    moveCompleted = false;
    startConveyor(direction);
}

void moveToSensor(int direction, int sensorPin) {
    if (conveyorRunning){
        // when already running, stop operation to configure the new running mode.
        stopConveyor();
    }
  stopAtSensor = true;
  sensorToStopAt = sensorPin;
  moveCompleted = false;
  startConveyor(direction);
}

void querySensors() {
  bool startSensor = digitalRead(START_SENSOR_PIN);
  bool endSensor = digitalRead(END_SENSOR_PIN);
  Serial.print("START_SENSOR:");
  Serial.print(startSensor ? "1" : "0");
  Serial.print(", END_SENSOR:");
  Serial.print(endSensor ? "1" : "0");
  Serial.print(", PULSE_COUNT:");
  Serial.println(pulseCount);
}

void startSensorISR() {
    if (stopAtSensor && sensorToStopAt == START_SENSOR_PIN){
            stopConveyor();
    }
}

void stopSensorISR() {
    if (stopAtSensor && sensorToStopAt == END_SENSOR_PIN){
            stopConveyor();
    }
}

void pulseCheck() {
  if (targetPulseCount > 0 && pulseCount >= targetPulseCount) {
    stopConveyor();
  }
}

void debouncePulse(){
    static uint8_t stable_count = 0;   // Count of consecutive stable readings
    static bool last_stable_state = digitalRead(PULSE_SENSOR_PIN); // Last confirmed stable state
    static bool last_read = last_stable_state;

    bool current_read = digitalRead(PULSE_SENSOR_PIN); // Read the raw button state

    // Check if the current reading is the same as the last reading
    if (current_read == last_read) {
        // Increment the stable count if state is consistent
        if (stable_count < DEBOUNCE_THRESHOLD) {
            stable_count++;
        }
    } else {
        // Reset the stable count if the state changes
        stable_count = 0;
    }
    // assign current_read to last_reading.
    last_read = current_read;

    // If stable count reaches threshold, confirm the new state
    if (stable_count >= DEBOUNCE_THRESHOLD) {
        // if this changed the state, increase the pulsecount
        if(last_stable_state != current_read){
            pulseCount++;
        }
        last_stable_state = current_read;
    }
}

void setElectroMagnet(int onOff){
    if(onOff){
        // 10% dutycycle.
        analogWrite(ELECTROMAGNET_PIN, 50);
    } else {
        analogWrite(ELECTROMAGNET_PIN, 0);
    }
}

void updateAngle(){
    static int i = 0;

    long time = micros();
    long angle_raw = angleMeter.read();
    angle = angle_raw*counts_to_deg;
    // halve the sample rate of the angular velocity
    angular_vel += counts_to_deg*float(angle_raw - prev_angle)/(float(time - prev_time)/1000000.0); //
    prev_time = time;
    prev_angle = angle_raw;
    if(i%15==0){
        // bit of averaging for smoothing
        angular_vel_smooth = angular_vel/15.0;
        angular_vel = 0;
    }
}

void printHuman(){
    Serial.print("A: ");
    Serial.print(angle); 
    Serial.print(",V: ");
    Serial.print(angular_vel_smooth);
    Serial.print(",W: ");
    Serial.println(wspeed);
}

// transmits serialized floats, as to not lose precision on other end.
void printMachine(){
  Serial.write(0x01); // start byte (start of heading)
  // everything else I'm sending are characters, so this should be fine to use.
  Serial.write((byte*) &angle, sizeof(float));
  Serial.write((byte*) &angular_vel_smooth, sizeof(float));
  Serial.write((byte*) &wspeed, sizeof(float));
}

// /*
// from https://forum.arduino.cc/t/what-is-the-easiest-way-to-run-some-code-each-millisecond-for-a-certain-amount-of-time/897345/3

// On AVRs, I've seen people enable one of the "Compare Match" interrupts on Timer0.
// This time is already running at about a 1ms rate (1/1024 s) till wrap-around, so any compare value will also interrupt every 1/1024 s.
// If you're not using PWM pins, you can set the compare register to an arbitrary value.
// If you ARE using PWM, whatever value is loaded by PWM will still cause an interrupt every 1/1024 s...

// For example: Adafruit_GPS/shield_sdlog.ino at master · adafruit/Adafruit_GPS · GitHub
// */
// void useTimerInterrupt(bool v) {
//   if (v) {
//     // Timer0 is already used for millis() - we'll just interrupt somewhere
//     // in the middle and call the "Compare A" function above
//     OCR0A = 0xAF;
//     TIMSK0 |= _BV(OCIE0A);
//     usingInterrupt = true;
//   }
//   else {
//     // do not call the interrupt function COMPA anymore
//     TIMSK0 &= ~_BV(OCIE0A);
//     usingInterrupt = false;
//   }
// }

// ISR(TIMER0_COMPA_vect) {
//     runDebounce = true;
// }

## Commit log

2025-01-29 Upload CAD source files
    [V-Slot Gantry.f3d, chain-link-ends.f3d, container-baseplate.f3d, conveyor-spacer.f3d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]
2025-01-29 Upload CAD 3MF exports
    [belt-holder(Mirror).3mf, belt-holder.3mf, cable carrier mount.3mf, chain-link-ends.3mf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]
2025-01-29 Upload arduino angle measurement sketch
2025-01-29 Add BOM
    [gantry-BOM.xlsx]
2025-01-29 Add KiCad files for Arduino shield
    [gantry-shield.kicad_pcb, gantry-shield.kicad_sch]
2025-01-29 Update BOM
    [gantry-crane-BOM.xlsx, gantry-shield-BOM.xlsx]
2025-01-30 Remove reference to printers
2025-01-31 Add arduino documentation.
2025-01-31 Add arduino documentation
2025-05-08 Add windspeed sensor to Arduino
2025-05-08 Add calibration script (deprecated)
2025-05-08 Update Arduino code to send uncompressed floats
2025-05-15 Update uarttest and arduino-shield
2025-06-30 Move crane Arduino to separate class
2025-07-08 Fix continuous logging and thread safety
2025-07-08 Folder structure update
    [belt-holder(Mirror).3mf, belt-holder.3mf, cable carrier mount.3mf, chain-link-ends.3mf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]
